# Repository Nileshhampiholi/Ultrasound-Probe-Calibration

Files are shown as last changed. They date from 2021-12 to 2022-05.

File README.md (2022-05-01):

# Ultrasound Probe Calibration

## Project Arbeit at MTEC Departmet TUHH

#### Author
1. Nilesh Hampiholi (nilesh.hampiholi@tuhh.de)

#### Project Guide
1. Johanna Sprenger
2. Stefan Gerlach

#### Superviser 
1. Prof. Dr. Alexander Schlaefer

## Abstract 

Ultrasound is utilized as medical imaging technology across multiple clinical diagnostic and therapeutic contexts primarily due to its availability and non-radioactive nature. Although 3D ultrasound probes have become increasingly accessible, most systems still employ 2D probes as they are highly efficient and affordable. Also, the 2D ultrasound images can be used to reconstruct the 3D ultrasound volume. One of the applications of ultrasound is to enable the practitioner to have a 3D visualization of the tissue, like a hologram displayed in real-time as an overlay over the practitioner’s field of view of reality. To accomplish the same, an ultrasound probe is swept across the area of interest, and the trajectory is recorded by the robot. The challenge is that the system records the end-effector pose and not the pose of the scan plane. Through calibration, the transformation matrix is established between the robot end-effector coordinate frame and the ultrasound probe frame. Current ultrasound calibration procedures usually demand freehand motions demanding human intervention, which restricts the application and integration with current robotic systems. This work presents a method for automatic robot-guided ultrasound probe calibration and volume scanning that is also efficient. The proposed method employs a wire phantom with four layers of N-shaped structure stacked one below the other. A UR3 lightweight robot and a Cepasonics ultrasound system are employed to perform the calibration. The overall calibration is accomplished in 500 seconds. An automatic segmentation algorithm identifies the markers with an accuracy of 0.3812 mm and 0.5670 mm in x and z directions. For spatial calibration, a combination of geometric method and iterative closest point algorithm is applied in coordination with a virtual point cloud phantom achieving a mean 3D localization error of 0.7049 mm. Through this procedure, sensor-to-robot calibration is accomplished with a mean translation and rotation error of 4.081 mm and 12.4308°.  Validation of the ultrasound probe calibration is achieved by reconstructing the surface of a 3D printed model phantom using 2D ultrasound images. Results demonstrated that the robot-assisted wire phantom calibration significantly improved the calibration repeatability and shorter data acquisition time.

## Calibration 

To run the calibration clone the repository 

Execute ---> main_US_Caliberation.m

Read the comments in the file to perform a fresh calibration. 

## File structure 

### move_robot

1. Contains config files used to while recording the images. Different config files are used to record data for wire phaantom and part phantom.

2. scan_wire_phantom.m scans moves the robot to 130 unique poses and recordes the images. 

3. scan_part phantom.m scans the part phantom takes about 120 images while moving in a straight line of steps 0.25mm.

4. requires network devices to be in the path.

### raw_data_to_US_image

1. Convet raw images to jpg images for part and wire phantom 

2. For a new calibration create a new folder trial_x. Copy all the raw files in this folder.

### image_segmentation
1. Stores all the jpg images.  

2. Segments all the images.  

3. Extract centiods from the images and stores in a csv files in following format [x y x y x y ....]. 

### create_virtual_phantom

1. creates a virtual phantom either with orign at wire of structure. 

### CAD- Model 
1. Contains 3d model of the wire phantom structure designed in fusion  360.

### registration_icp 

1. Computes trasfromation between the probe frame and wire phantom frame using ICP algorithm. 

2. Stores the transformation in csv file.

### registration_geometry

1. Computes trasfromation between the probe frame and wire phantom frame using geometric method. 

2. Stores the transformation in csv file.

### 3D reconstruction

1. Scans through all the images of the segments them. 

2. From the segments images the high intensity pixels are extracted to generate point clouud.

3. Trasfrom the point cloud using hand eye calibration results. 

### solve_ax_yb
1. Solves hand eye calibration (AX=YB) using QR24 algorithm. 

### robot_poses 

1. Stores all the poses of the robot while recording data. 

### papers

1. Contains all the research papers reffered.

### project_presentation 
1. Contains mid term and final presentation.

### project_report 

1. Contains final report.

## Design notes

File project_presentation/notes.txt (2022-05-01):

Slide 1 - Project name 

Good evening every one. My topic for the project arebiet is Robot Guided Ultrasound Probe caliberation and volume scanning.

Silde 2 - Project overview 
THIS  ARBEIT IS PART OF THE PROJET - 
Let me start by giving  a breif overview of the whole project and then talk about the parts I am working on in Detail

This is divided into sub module which are ......read slides 

I am working o Caliberation of lInear probe  and augementation of 2d scans to 3d volume.  

Slide 3 - Motivation and goals

Guided interventions are a way to help physicain  virtually visualise the target in surgical sight for needle insertions or 
isualisepath way for an aspiration.

Exisiting solution concentrate on free hand probe caliberation using external trackers and cameras. 

In order to enable guided assistance US volume has to be scanned and trasfromed in meaning full way which requires the postion of 
the probe to be known with respect to world cordinates.

Position can determined by Caliberation.

After caliberation 2d scans can be agumented into 3d volume.

Slide 4 - Methodology 

Lets dicuss the work flow the project. 

I  started with the  design of caliberation phantom ( z wire or n wire phantom )

Aquire Images of the caliberation phantom 

Segment the aquired images 

Extract markers  from segmented images

Estimate the pose 

Caliberate the probe 

Agumentation 

Slide 5 - Hand eye caliberation

This is the basic overview of the hand eye calibration 
A = is obtained by forward kinematics  (TF from robot base to end effector)

B = TF from phantom cordinate frame to US probe Cordinate from 

X = TF from robot end effector to US probe 

Slide 6 - Design of Calibration phantom

I designed the phantom  in fusion 360 and printed it using 3d printer. 

Its  10 cms in height 15 cms in width and 10 cms in height

The holes are 10mm apart in both directons 

Using a fishing wire to create the n or z shape. As the wire due to its properties can be easily. 

I am using 4 layers with 3 in same direction and 4 in different direction

I created a point cloud model imitating the same. 

Slide 7 - data aquitision and segmentation 

Capturing US images can be quite challeing. As it is very sensitive. 

Airbubble and bust particles are external problems. 
Also the base while capturing should be a matrial that desnt not reflect sound much. 

Shown is the 1st capture the base and instersection of wire with imae plane is seen 

After playing with the parameters in the supra interface I was able to obtain clean images that are easy to segment. 
(Parameters to control the witdth of the beam that is emmitted and also to what depth)  

Still is it chanllenging to segment the markers that are close to each other.

I applied 

Median filter and Noise removal by filtering groups of 10 or less pixels and then morphoogial operation this helps
 to seprate blobs close to each other 

(median filter - removes noise by averaging with pixels in the neighbor hood  I used kernel size of 7)

I obatined good results as shown in the next slide 

Slide -8  Marker extraction 

To extract the marker points I used the matlab vision toolbox and used the built in functions 

Also I used kmeans algorithm to identify 12 clusters and provide centriod of the clusters 

Both methods leads to almost same results.

Slide 9  - Pose Estimation 

This is the most challenging part of the Caliberation process. 

Find a trasfrom from the wire phantom to the US Probe frame 

The images obatined are in 2d and represent only one x-y plane of the phantom. 

These markers are to be  mappped or registered to 3d phantom. 

The structure of the wire phantom can be exploited here. 
Available distance ratios match the markers to the phantom. 

I am currently iterating one plane of phantom and matching the points and computing the trasfrom and estimate the mean error. 

As long as the error is decreasing iterations continue if the error increases from previos iteration the loop stops 

I able to to achinve mean estimation error of the 0.76mm

Slide 10 - Pose estimation results 

Here we can see the markers captured from US probe are trasformed to match the phantom.  

This trasfromation can be used to perform hand eye calibration. 

Slide 11 - upcoming taskes 

In the future i will work twards solving the hand eye problem and and obatin 3d volume by scanning the show object. 

Slide 12 

Thank you. If you have any questions or suggestions I would be pleased

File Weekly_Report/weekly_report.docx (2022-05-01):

Weekly Report

Name: Nilesh Hampiholi

Matriculation No.: 54811

Topic: Robot Guided Surface Scanning with Ultrasound

Date: 25|2|2022

Tasks Done:

- I completed the calibration and the image reconstruction part
- For image reconstruction the images are segmented and then the pixels are treated as points to obtain a point cloud and I plot them as a surface. I have added a figure at the bottom for reference.

Issues:

- The calibration results are really bad. I tried to sample the collected data but the results don’t improve.
- I think I have made a mistake during data acquisition as I captured the images along the whole length of the phantom.
- Also, since I am generating a point cloud of the 3d part I have to scan it from multiple angles to cover all the faces.

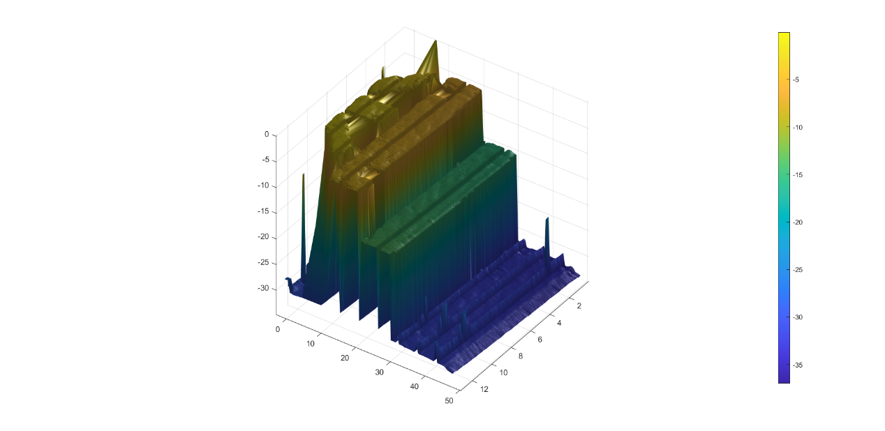
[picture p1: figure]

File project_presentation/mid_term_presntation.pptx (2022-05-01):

## Nilesh Hampiholi

Robot - Guided Ultrasound Probe Calibration and Volume Scanning

## Project Environment

- Ultrasound image-guided puncture supported by augmented reality (AR)
  - Calibration of linear probe to maker/ robot
  - Augmentation of 2D US images into 3D volume
  - Derive motion profiles of US probe and patient
  - 3D Rendering of the structures under the skin into AR glasses
  - Localizing the target using the scan
  - Needle placement

## Motivation and Goals

- Motivation
  - Tracked ultrasound imaging is an inexpensive, safe, non-invasive technique for several guided interventions such as needle insertions, biopsies and ablations
  - Existing solution concentrate on free hand probe calibration using external trackers and camera
- Goals
  - Calibration of linear probe to maker/ robot
    - To enable assistance, US volume of the patient is needed
    - To obtain the volume, position of probe has to be determined accurately
    - Position is computed by calibration
  - Augmentation of 2D US scans into 3D volume

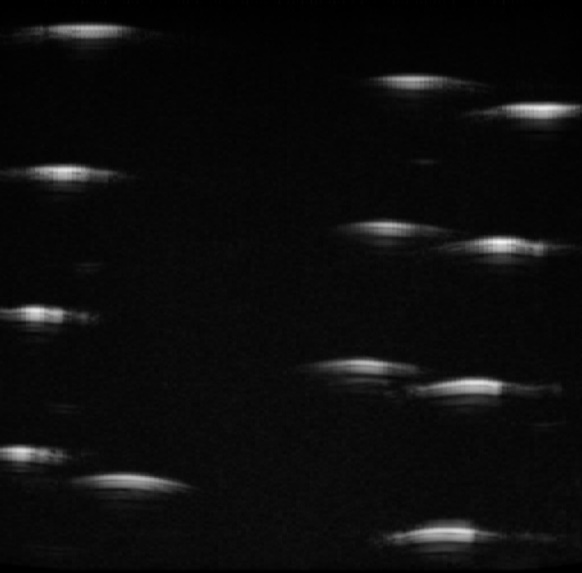
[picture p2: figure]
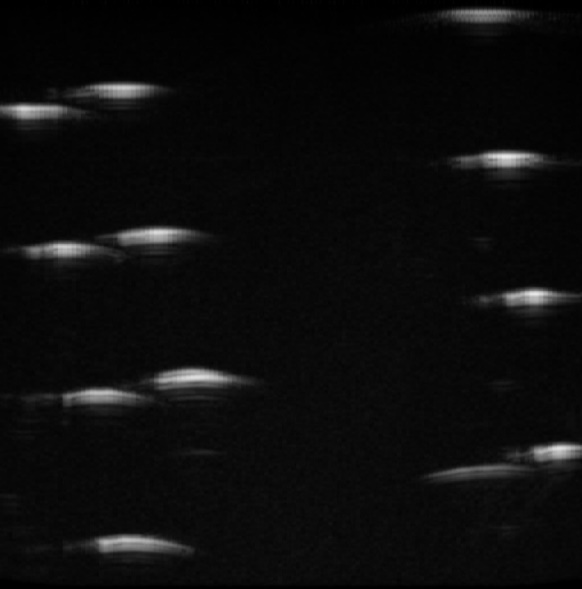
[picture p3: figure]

US Scan from
different angles

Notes: Not very sure about the motivation.

## Methodology

- Design calibration phantom
- Data acquisition
- Semantic segmentation
- Extraction of centroids from segmented markers
- Pose estimation
- Solve hand eye problem
- Image stitching to obtain 3D US-volume

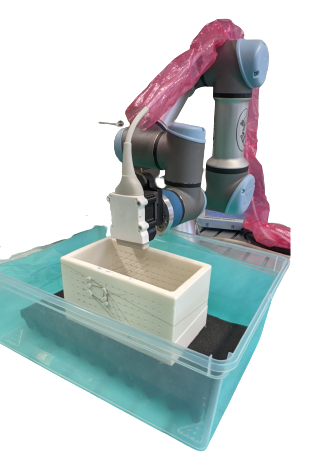
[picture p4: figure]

Experimental Set-up

UR-3 Robot
US Probe
Wire Phantom

## Hand Eye Calibration

- Location of probe and scanning object is unknown with respect to robot base or world coordinates
- Determining the transformation between robot end-effector and a sensor
- Solve AX=XB to obtain pose of phantom in robot base coordinate frame

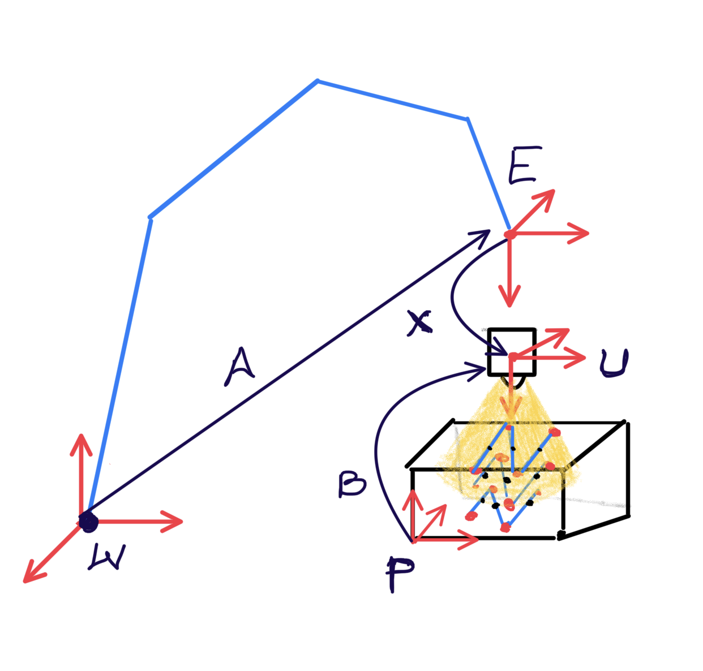
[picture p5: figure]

## Design of Calibration Phantom

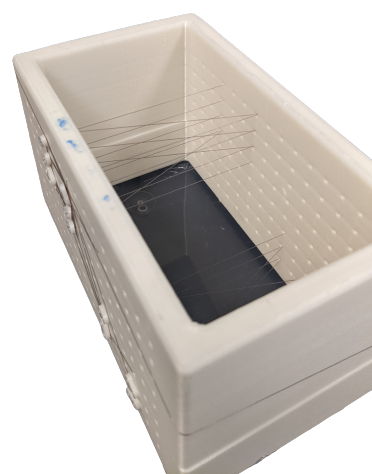
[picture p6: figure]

(a) 3D Printed Calibration Phantom 15 x 5 x 10 cm

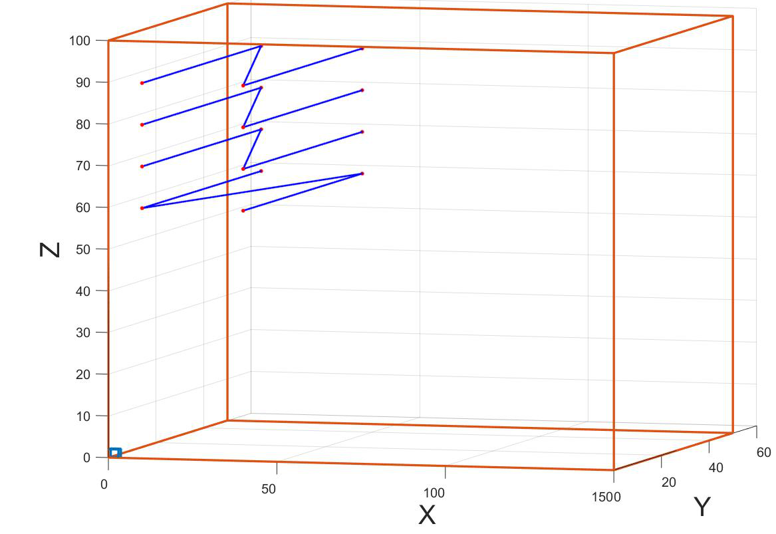
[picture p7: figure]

(c) Point Cloud model of the Calibration Phantom

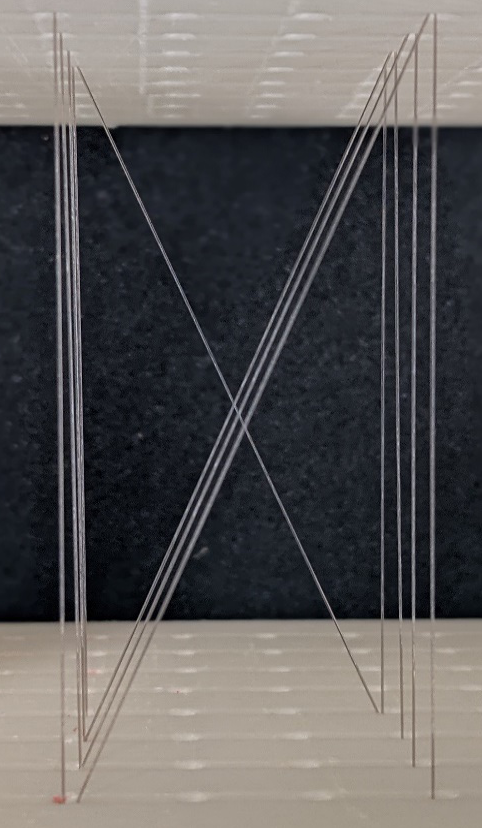
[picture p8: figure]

(b) Fishing Wires arranged in N – shape with 4 layers

## Data Acquisition and Segmentation

- Acquiring good ultrasound scans is challenging
  - Air bubbles
  - Small dust particles
  - Sensitive probes
- Segmenting markers very close to each other is difficult.
  - Median filter
  - Noise removal
  - Morphological operation

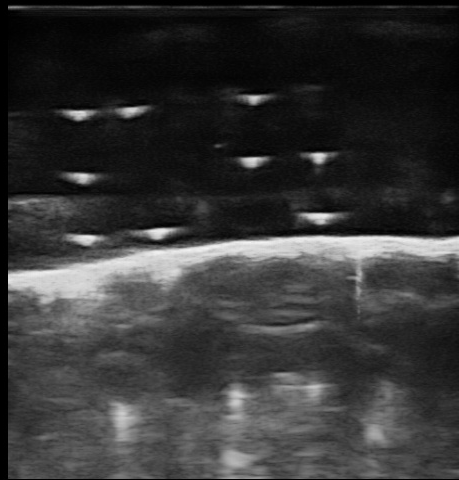
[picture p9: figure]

Intersection of Wire with Image Plane

Base of the Phantom

Initial US Scan

## Segmentation Results

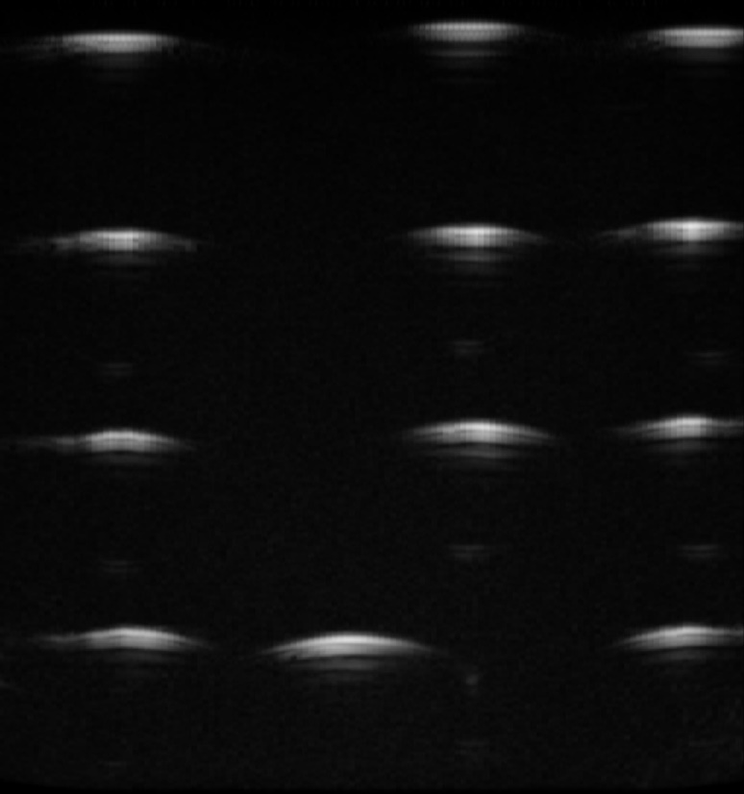
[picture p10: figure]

(a) Acquired Images

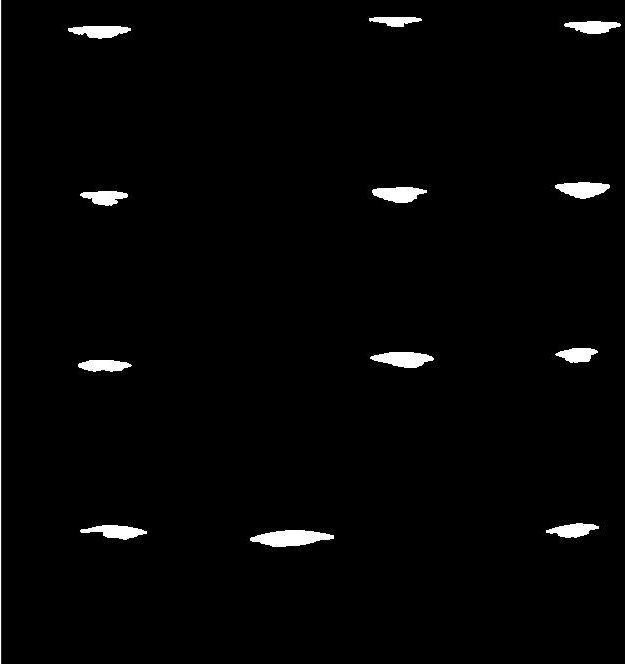
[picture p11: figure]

(b) Segmentation Results

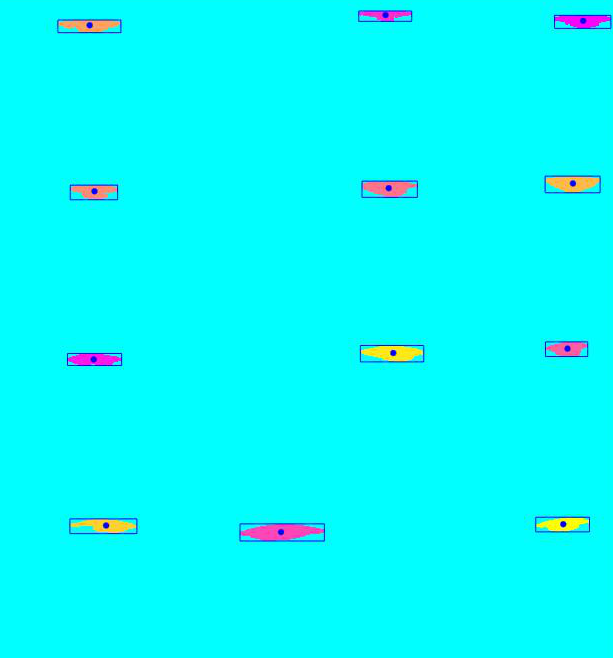
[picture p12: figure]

(c) Extracting centroids from segmented markers

Centroids

## Pose Estimation

- Pose estimation is challenging for US scans due to mapping 2D image to 3D phantom
- Transformation from phantom coordinate frame to the US probe coordinate frame
  - Match the segmented markers to the point cloud model of the phantom
  - Obtain the matching correspondences
  - Compute the transformation between matched phantom points and marker points
  - Calculate pose estimation error
- Mean pose estimation error = 0.76mm

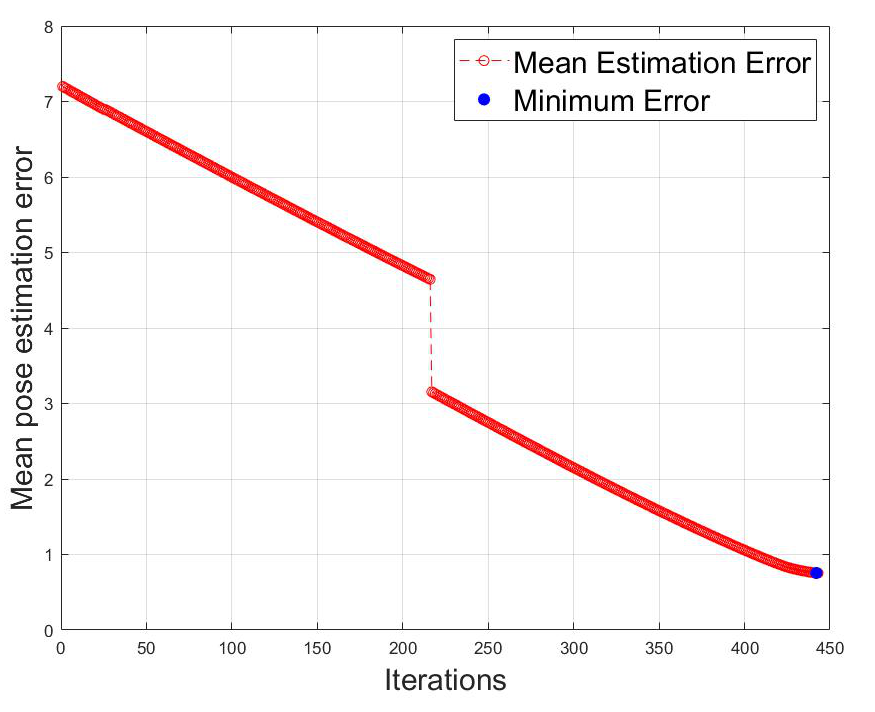
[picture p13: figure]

## Pose Estimation Results

- Initial Data

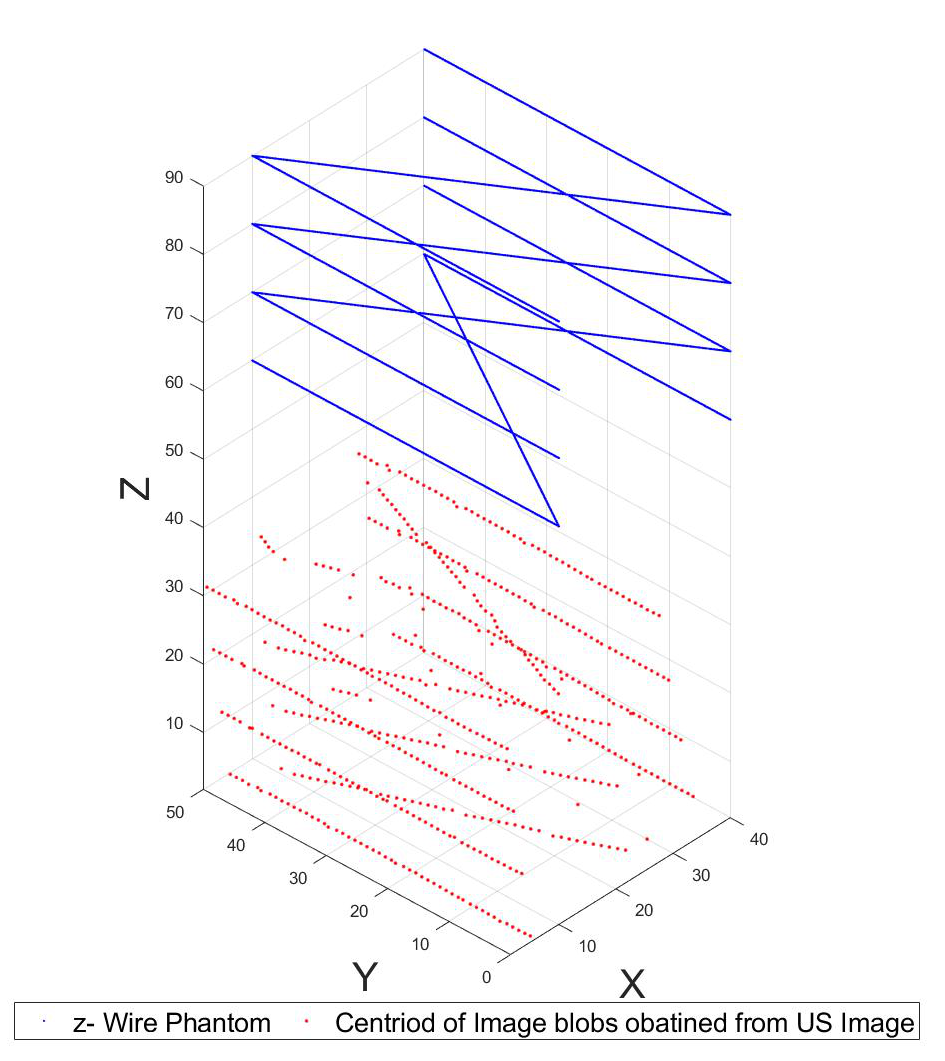
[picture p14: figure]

- Transformed Data

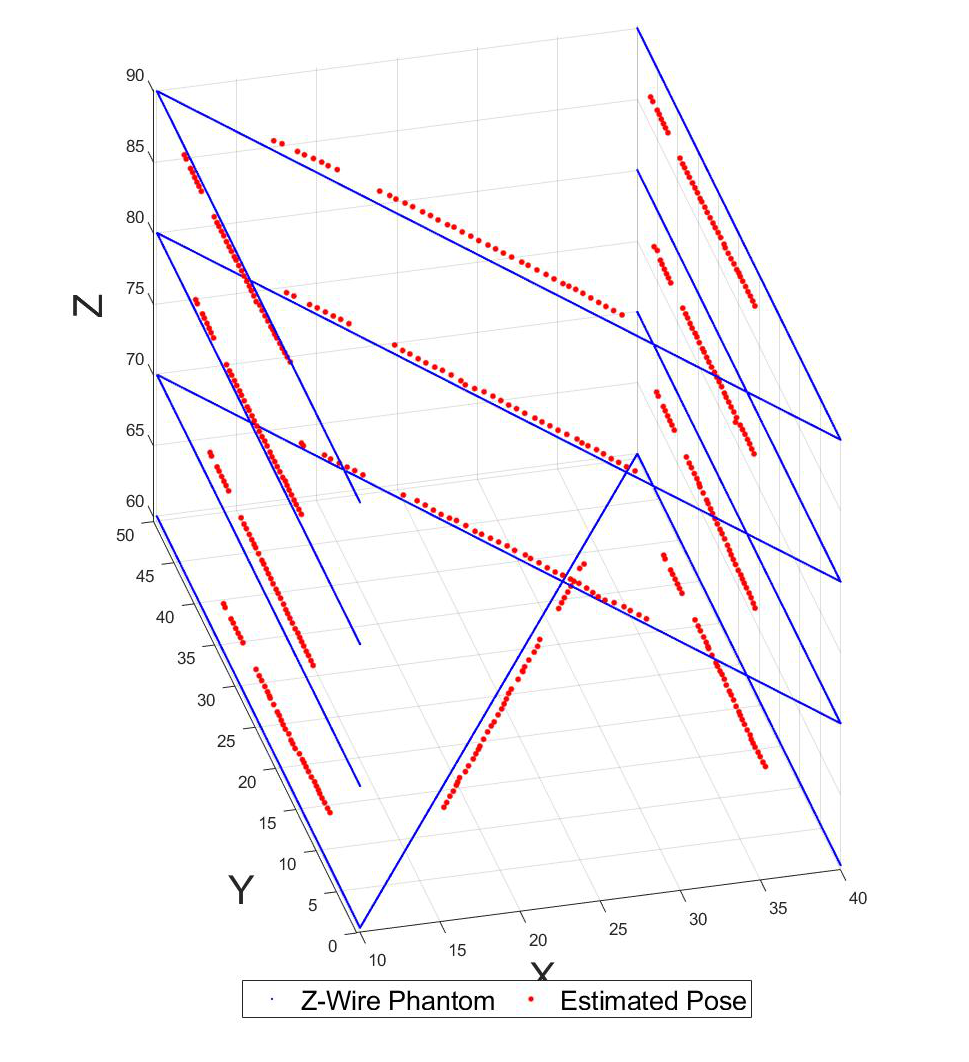
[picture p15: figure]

## Upcoming Tasks

- Solve hand eye calibration
- Creating 3D volume using image stitching techniques
  - Using the calibrated US probe scan the shown objects.
  - Measure the 3D objects and evaluate the results.

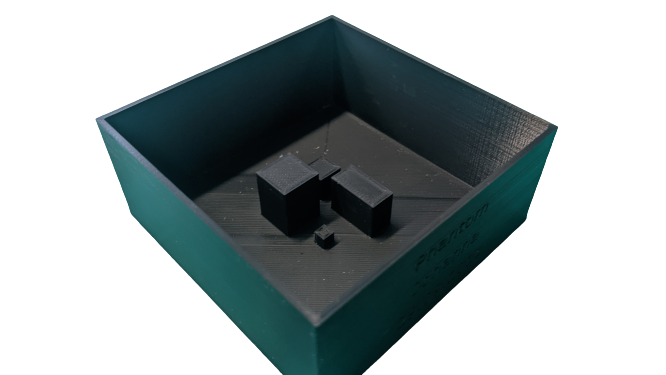
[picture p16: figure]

Objects

## Thank you

## Pose Estimation Plane Wise

- Iteratively feed one plane of the phantom
- Commute the transformation between segmented markers and static phantom plane
- Transform the markers
- Compute mean Euclidian distance between markers and correspondence phantom points
- Choose the transformation that yields least distance
- Pose estimation error = 0.76mm
- Limitations :
  - Case of rotation along X and Z axis is not considered

## Pose Estimation using Distance Ratio

- Compute the distance ratio of the markers for every layer
- Compute the distance ratio for the phantom
- Match the distance ratio for every layer separately
- This gives the approximate location of the image plane in phantom coordinates
- Use ICP to compute the transformation in the small region of the phantom model
- Pose estimation error = 1.05mm
- Limitation:
  - Rotation along Z axis is difficult to estimate.

d_image = α_1/ α_2

α_1
α_2

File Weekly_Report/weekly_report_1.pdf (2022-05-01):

Weekly Report

Name: Nilesh Hampiholi

Matriculation No.: 54811

Topic: Robot Guided Surface Scanning with Ultrasound

Date: 14|05|2021

Tasks Done:

- Research on Ultrasound
- Research on Calibration using Ultrasound

Questions:

- You mentioned I will be getting some ID and password by when will I be receiving that?
- Can I get some research papers or link that you guys are referring?

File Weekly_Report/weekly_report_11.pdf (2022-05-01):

Weekly Report

Name: Nilesh Hampiholi

Matriculation No.: 54811

Topic: Robot Guided Surface Scanning with Ultrasound

Date: 20|10|2021

Tasks Done:

- I have completed he segmentation of the images
- Also extracted centroids
- I have done some progress with respect to point matching using ICP but not there yet.
- Here is sample of Image segmentation.

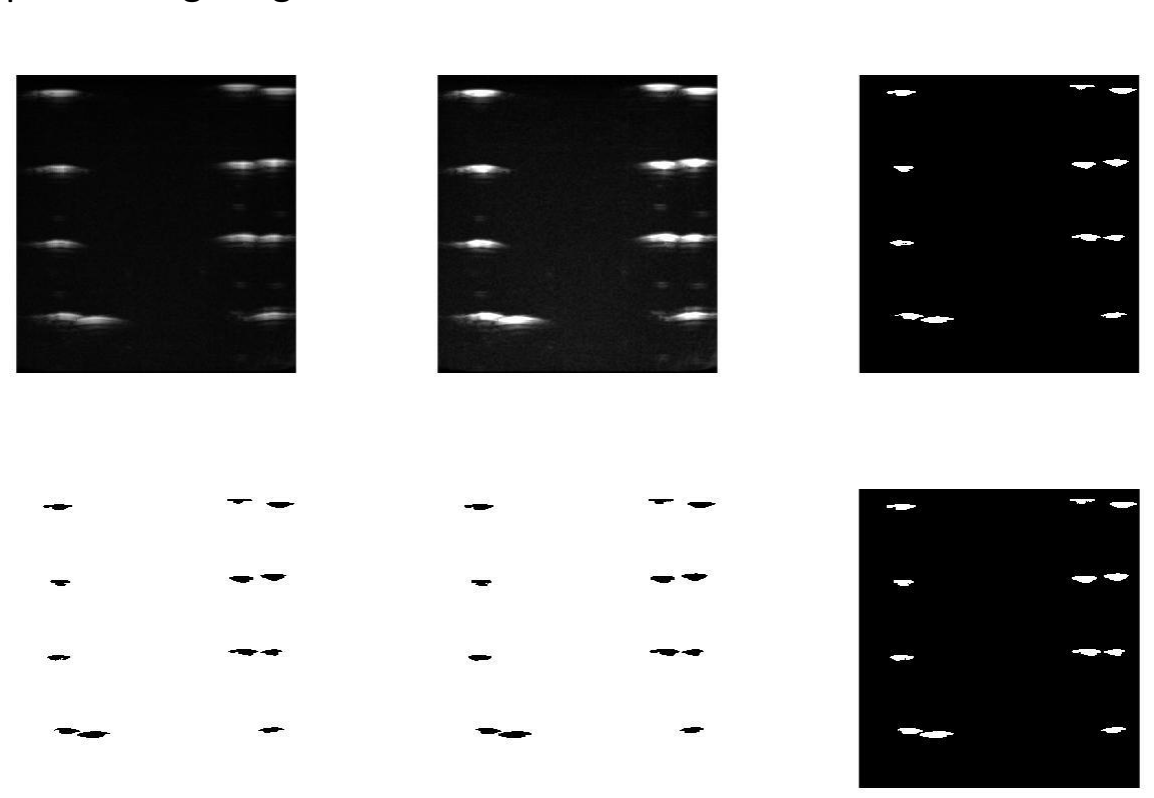
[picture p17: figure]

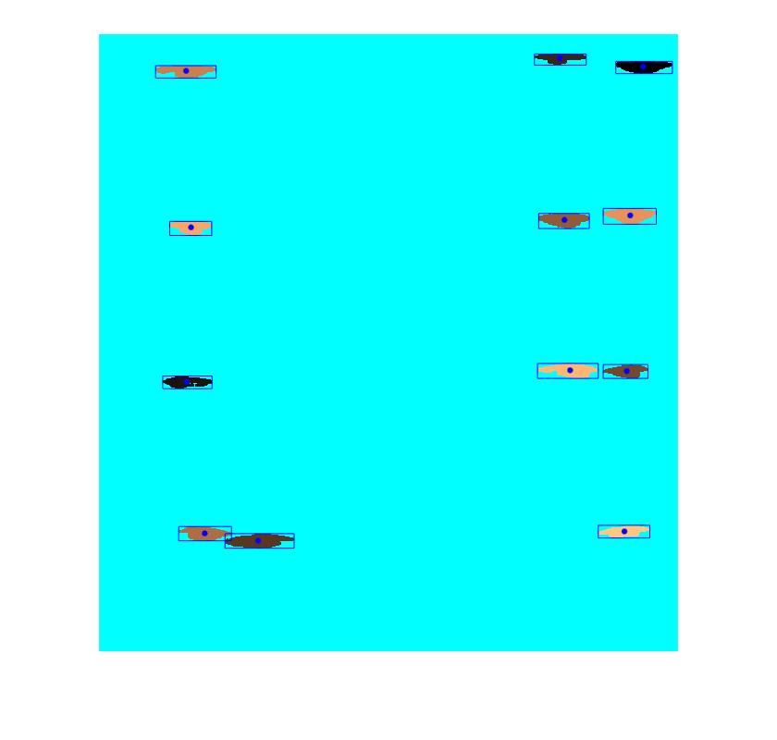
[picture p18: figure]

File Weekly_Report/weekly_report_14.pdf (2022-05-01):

Weekly Report

Name: Nilesh Hampiholi

Matriculation No.: 54811

Topic: Robot Guided Surface Scanning with Ultrasound

Date: 29|11|2021

Tasks Done:

- I took new image from different angles last week.
- Processed them and matched with the wire phantom
- I adjust the scaling values and the average pose estimation error is about 0.5mm
- I also solved AX=XB but I think I am getting it wrong.
- I am using the following scheme

A = Forward kinematics

B = Inverse of the pose estimation computed from ICP (Also tried without taking the inverse)

This the resulting matrix I am getting. It does not make much sense to me.

- I am also attaching the code I use to solve it.

1.0e+08 *

-0.0000 -0.0000 -0.0000 5.5497

-0.0000 -0.0000 0.0000 1.7082

-0.0000 0.0000 0.0000 2.8169

0 | 0 | 0 0.0000

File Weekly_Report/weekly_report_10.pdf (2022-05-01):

Weekly Report

Name: Nilesh Hampiholi

Matriculation No.: 54811

Topic: Robot Guided Surface Scanning with Ultrasound

Date: 27|09|2021

Tasks Done:

- Modelled the phantom and gave it for 3d printing.
- I have written a function to get the distance between the centroids
- The phantom looks something like this.

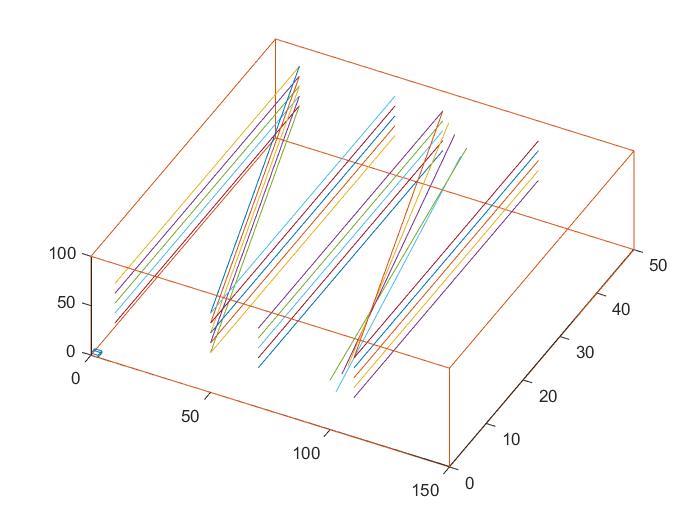
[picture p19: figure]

Question Description:

- So, the paper uses RANSAC approach to fit the data into rectangles and then classify the points as left strand, middle strand and right strand points.
- Then again uses RANSAC to fit a plane through 3d points of the middle strand.
- The using the model paraments of the fit find a projection and estimate the x, y, z translation from image to phantom.

- I find it pretty similar but I am not able to corelate yet.
- Should I try implementing this or do you have any paper where I can find better theory to implement.
- Paper also does not find angles explicitly by geometric method.

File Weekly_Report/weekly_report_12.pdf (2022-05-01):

Weekly Report

Name: Nilesh Hampiholi

Matriculation No.: 54811

Topic: Robot Guided Surface Scanning with Ultrasound

Date: 20|10|2021

Tasks Done:

- I have implemented ICP algorithm using 3 different methods.
- But its not yet yielding any good results.
- I have tried multiple options by changing the parameters in the algorithm.
- Results looks as follows

•

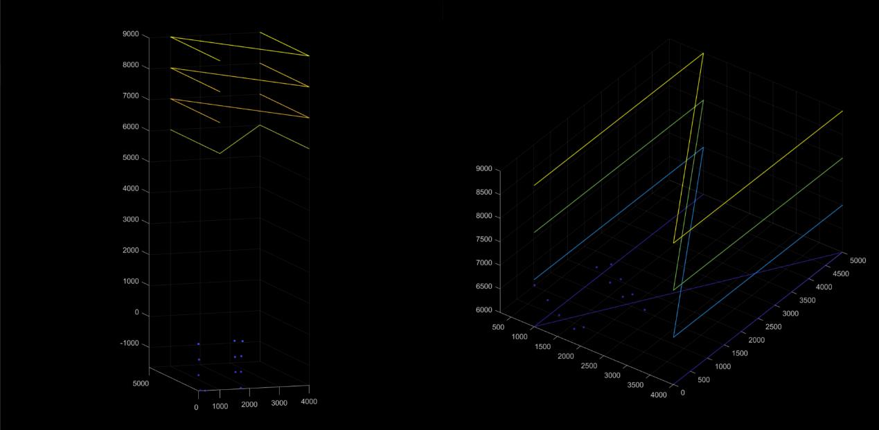
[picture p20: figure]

- Results look similar for all the approaches.
- Am I doing something wrong?


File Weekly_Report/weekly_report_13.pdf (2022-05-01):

Weekly Report

Name: Nilesh Hampiholi

Matriculation No.: 54811

Topic: Robot Guided Surface Scanning with Ultrasound

Date: 20|10|2021

Tasks Done:

- I have implemented ICP algorithm using 2 different methods.
- Both yield good results
- 1

st method matches the points plane vise
- 2

nd method uses the distance ratio and then use only the matched points to get the transformation
- Translation is x, y, z is achieved with good accuracy.
- Also, I think rotation along x and y direction also works well.
- But I am not sure about the rotation along z axis.

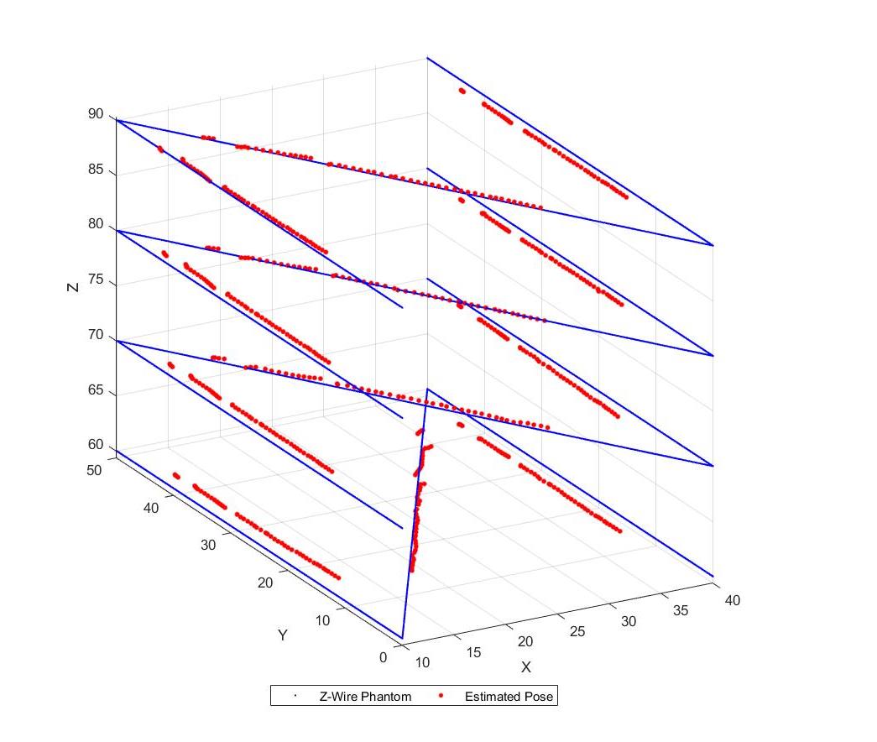
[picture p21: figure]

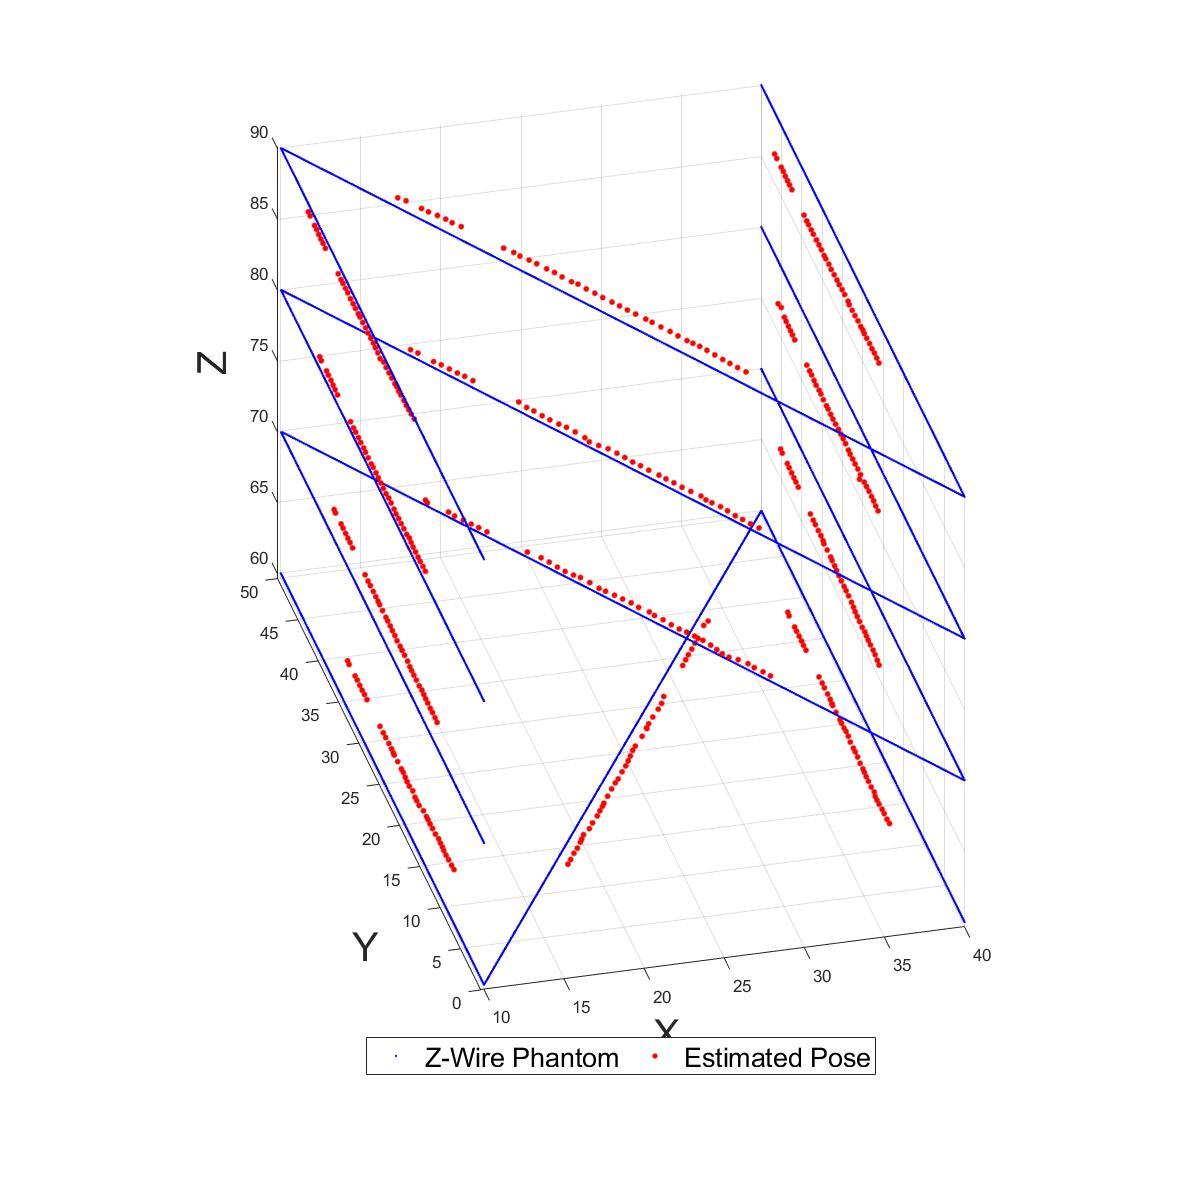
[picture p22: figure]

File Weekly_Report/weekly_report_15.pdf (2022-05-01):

Weekly Report

Name: Nilesh Hampiholi

Matriculation No.: 54811

Topic: Robot Guided Surface Scanning with Ultrasound

Date: 13|12|2021

Tasks Done:

- I have implemented the QR24 algorithm.
- The Results now make some sense.

Here is the Calibration Matrix I obtained.

X_q =

-0.0000 -0.2529 0.1605 -0.9541

0.0001 0.1406 -0.9696 -0.2004

0.0000 -0.9572 -0.1848 0.2226

-1.0000 0.0000 -0.0001 -0.0000

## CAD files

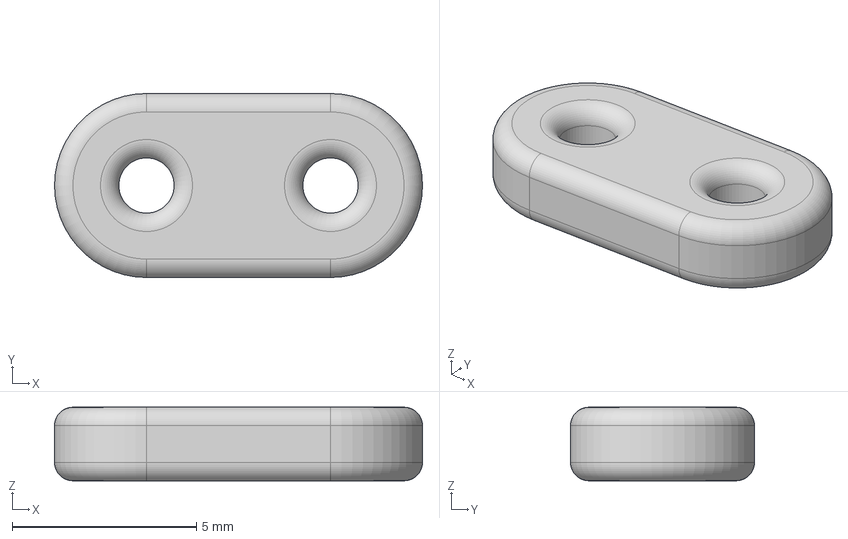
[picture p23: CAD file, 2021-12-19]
CAD-model/wire_hold_print_qty_20 v1.step
10.0 x 5.00 x 2.00 mm

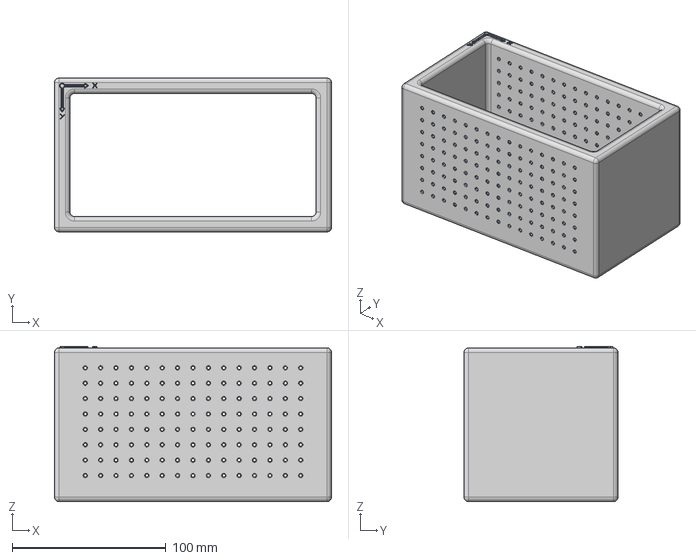
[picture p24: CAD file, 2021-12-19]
CAD-model/Phantom_1 v2.step
180.0 x 100.0 x 101.0 mm

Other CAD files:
CAD-model/Phantom_1 v2.f3d
CAD-model/wire_hold_print_qty_20 v1.ipt

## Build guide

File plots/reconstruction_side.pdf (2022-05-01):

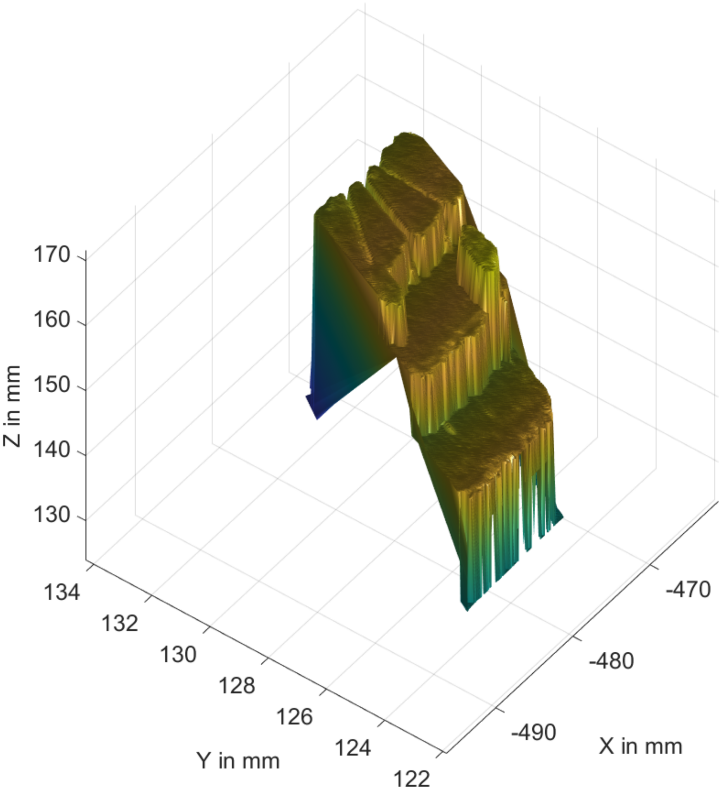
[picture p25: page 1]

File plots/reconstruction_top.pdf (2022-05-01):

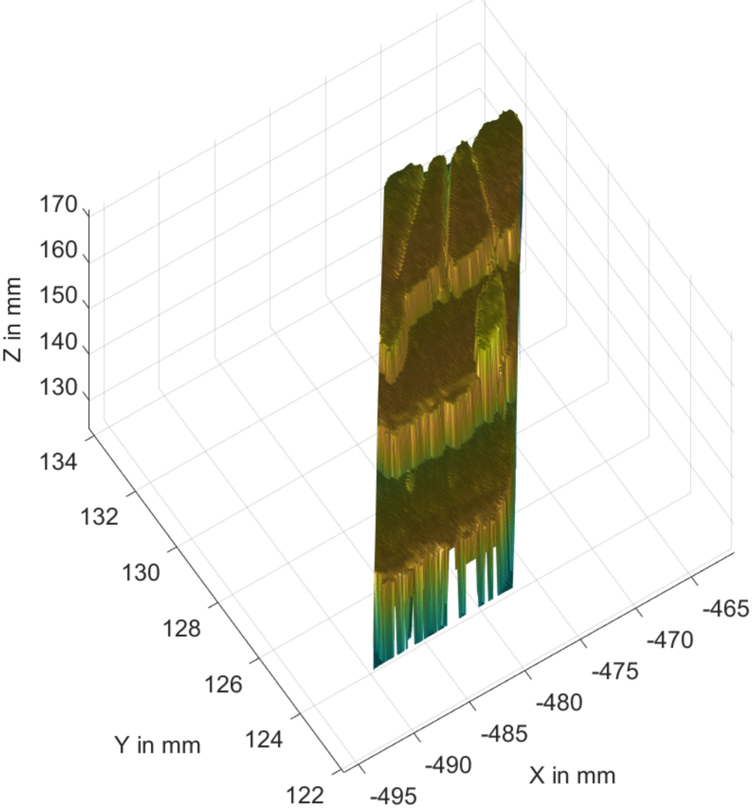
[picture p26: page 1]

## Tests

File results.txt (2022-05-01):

Overall Transformation: 
Mean translation error: 0.8178 mm
Mean translation error after orthonormalization: 4.081 mm
Mean rotation error: 9.4777 degrees
Mean rotation error after orthonormalization: 12.4308 degrees
Mean Fro. Norm: 1.5462
Mean Fro. Norm after orthonormalization: 4.2358

1
Overall Transformation: 
Mean translation error: 0.93658 mm
Mean translation error after orthonormalization: 4.1932 mm
Mean rotation error: 9.67 degrees
Mean rotation error after orthonormalization: 12.3538 degrees
Mean Fro. Norm: 1.5728
Mean Fro. Norm after orthonormalization: 4.3101

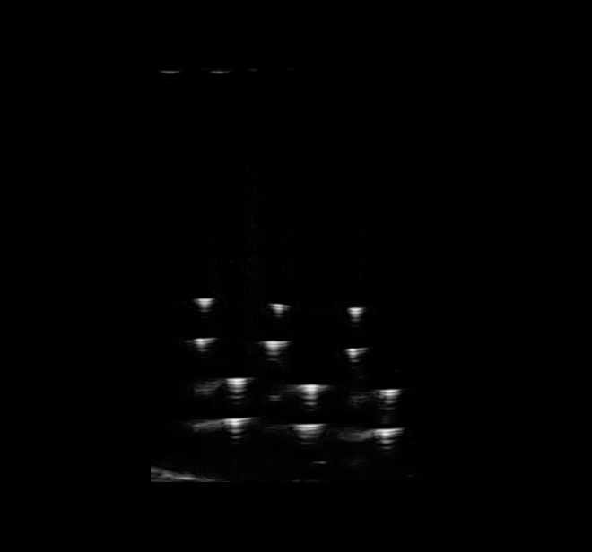
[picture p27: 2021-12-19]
network-devices/ultrasound/RobotUltrasoundCalibration/_images/3/fileoutpos.txt_35.jpg

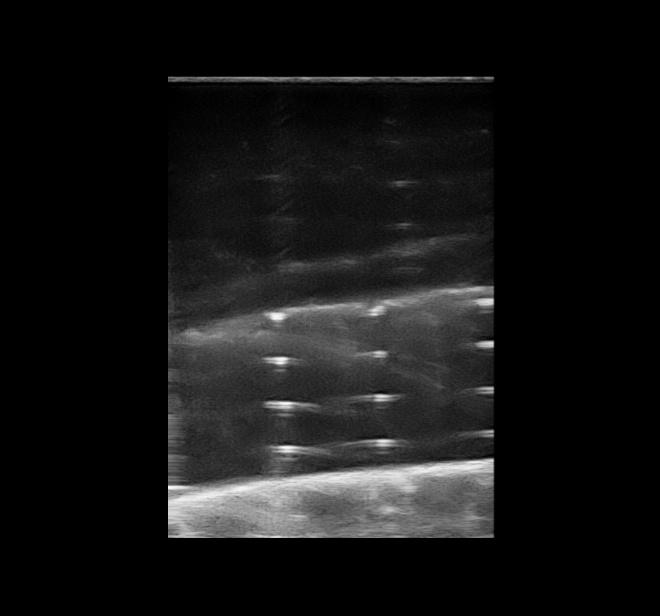
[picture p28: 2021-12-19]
network-devices/ultrasound/RobotUltrasoundCalibration/_images/1/fileoutpos.txt_3.jpg

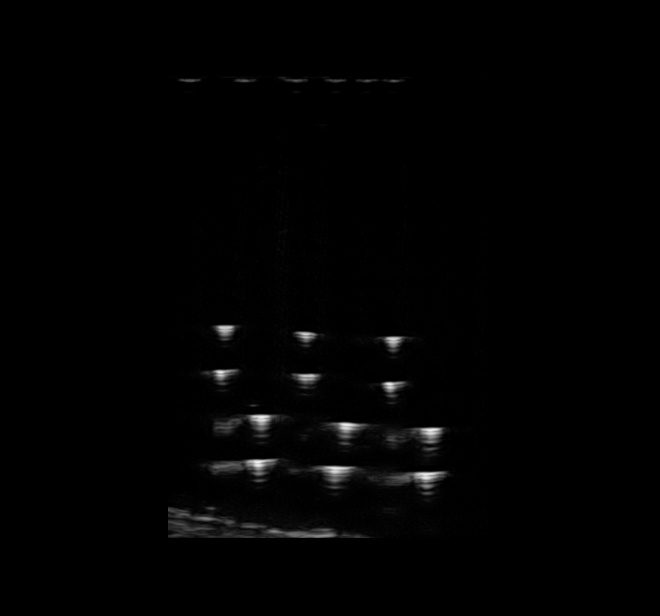
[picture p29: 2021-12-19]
network-devices/ultrasound/RobotUltrasoundCalibration/_images/3/fileoutpos.txt_10.jpg

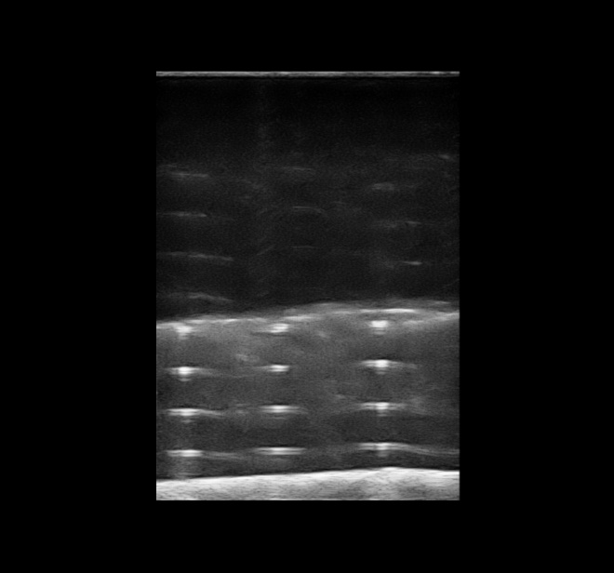
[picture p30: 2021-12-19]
network-devices/ultrasound/RobotUltrasoundCalibration/_images/1/fileoutpos.txt_10.jpg

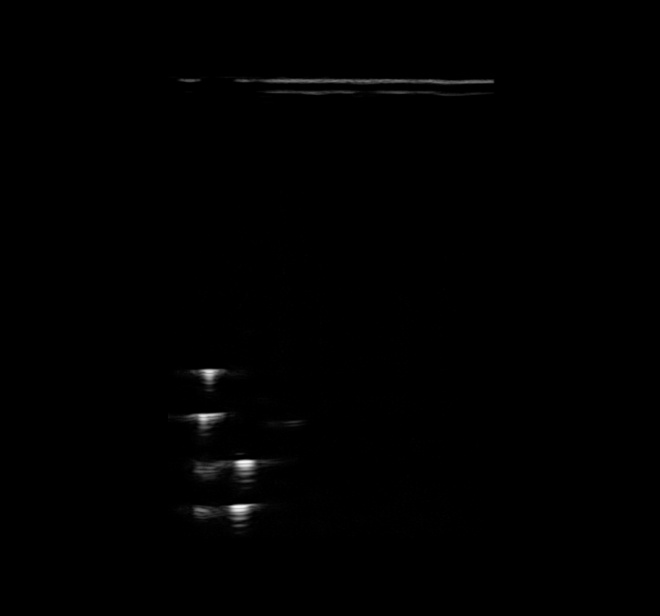
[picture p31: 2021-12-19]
network-devices/ultrasound/RobotUltrasoundCalibration/_images/3/fileoutpos.txt_14.jpg

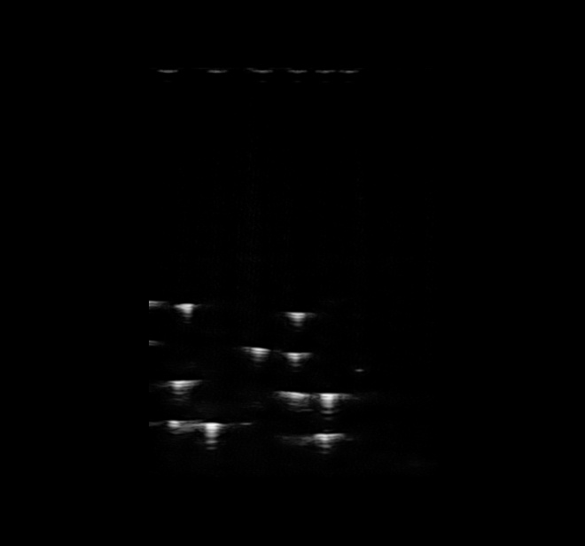
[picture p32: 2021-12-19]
network-devices/ultrasound/RobotUltrasoundCalibration/_images/3/fileoutpos.txt_6.jpg

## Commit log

2021-12-19 Fist Commit
    [centriods.csv, errors.csv, image_poses.csv, image_poses_left.csv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]
2021-12-19 Adding Cad files
    [Phantom_1 v2.f3d, Phantom_1 v2.step, wire_hold_print_qty_20 v1.ipt, wire_hold_print_qty_20 v1.step]
2022-04-30 resolving issues
    [centriods.csv, errors.csv, image_poses.csv, image_poses_left.csv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]
2022-05-01 resolving conflicts
    [try_5.csv, try_6.csv]
2022-05-01 solving git issues
    [wire_phantom.csv]
2022-05-01 adding network devices
2022-05-01 adding files
    [registration_poses.csv]
2022-05-01 adding segmentation
    [centriods.csv, errors.csv]
2022-05-01 adding additional documents
    [part.csv, part_left_depth10.csv, part_right_depth10.csv, part_straight.csv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]
